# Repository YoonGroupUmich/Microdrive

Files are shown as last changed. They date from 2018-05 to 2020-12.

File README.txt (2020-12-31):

Microdrive designs for silicon probes.

Assembly instructions can be found in the assembly_instructions_rat1-2inch_v20.pdf file or at these links:
1. Microdrive assembly:  https://youtu.be/rjxaH515N64 
2. Probe attachment to microdrive:  https://youtu.be/2L5RHcbsU7o 
3. Probe recovery:   https://youtu.be/T5gyuZVKXo8 

The .stl files are optimized for Formlabs Form2 printer and Grey-v4/Clear-v4 Resin. For other printers and/or resins, some modifications may be necessary.

1 version is made available here:
v21: shell base 3.2 x 7.5 mm (WxL); height: 16 mm; travel distance 4.8 mm

This microdrive was modified based on Hiroyuki Miyawaki's design. The latest version of his microdrive is available at https://github.com/Mizuseki-Lab/microdrive.

The original idea of the drive is described in the following paper.

Micro-drive and headgear for chronic implant and recovery of optoelectronic probes Jinho Chung, Farnaz Sharif, Dajung Jung, Soyoun Kim & Sebastien Royer Scientific Reportsvolume 7, Article number: 2773 (2017) doi:10.1038/s41598-017-03340-5 https://www.nature.com/articles/s41598-017-03340-5

The designs are desitributed under GNU GPLv3 license.

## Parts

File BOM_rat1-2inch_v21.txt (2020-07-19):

Rat drive (1/2")

Qty	Name			Vendor		Item number		Notes			Link

7	00-90 nut		McMaster	92736A112					https://www.mcmaster.com/92736a112
2	00-90 screw 1/2"	McMaster	92482A235					https://www.mcmaster.com/92482a235
4	00-90 screw 1/4"	McMaster	93701A005					https://www.mcmaster.com/93701a005
1	rectangular header	DigiKey		SAM1067-40-ND					https://www.digikey.com/products/en?keywords=SAM1067-40-ND

1	T2 screwdriver		McMaster	52995A31		Only T2 is necessary!	https://www.mcmaster.com/52995a31
1	00-90 tap		McMaster	2504A14						https://www.mcmaster.com/2504a14
1	1.2 mm drill bit	McMaster	2958A29			Use to remove excess 	https://www.mcmaster.com/2958a29
									resin for 00-90 screws
									(if necessary).

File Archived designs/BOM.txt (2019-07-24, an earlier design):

Mouse drive

Qty	Name
3	00-90 nut (McMaster: 92736A112)
2	00-90 screw 3/8" (McMaster: 92453A856)
1	rectangular header (DigiKey: SAM1067-40-ND)

Rat drive (1/2")

Qty	Name
3	00-90 nut (McMaster: 92736A112)
2	00-90 screw 1/2" (McMaster: 92482A235)
1	rectangular header (DigiKey: SAM1067-40-ND)

Rat drive (5/8")

Qty	Name
3	00-90 nut (McMaster: 92736A112)
2	00-90 screw 5/8" (eBay: 00-90 X 5/8 Slot Fillister Head Machine Screws SS)
1	rectangular header (DigiKey: SAM1067-40-ND)

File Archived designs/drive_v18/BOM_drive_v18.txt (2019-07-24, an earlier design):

Rat drive (1/2")					
			
Qty	Name			Vendor		Item number	Notes			Link
					
7	00-90 nut		McMaster	92736A112				https://www.mcmaster.com/92736a112
2	00-90 screw 1/2" 	McMaster	92482A235				https://www.mcmaster.com/92482a235
4	00-90 screw 1/4" 	McMaster	93701A005				https://www.mcmaster.com/93701a005
1	rectangular header	DigiKey		SAM1067-40-ND				https://www.digikey.com/products/en?keywords=SAM1067-40-ND

Additional tools				
1	T2 screwdriver		McMaster	52995A31	Only T2 is necessary!	https://www.mcmaster.com/52995a31
1	00-90 Premium Tap 	Amazon							https://www.amazon.com/
1	1.2 mm drill bit	McMaster	2958A29		Any 1.2mm drill bit. 	https://www.mcmaster.com/2958a29
								Use to remove excess 
								resin for 00-90 screws 
								(if necessary).

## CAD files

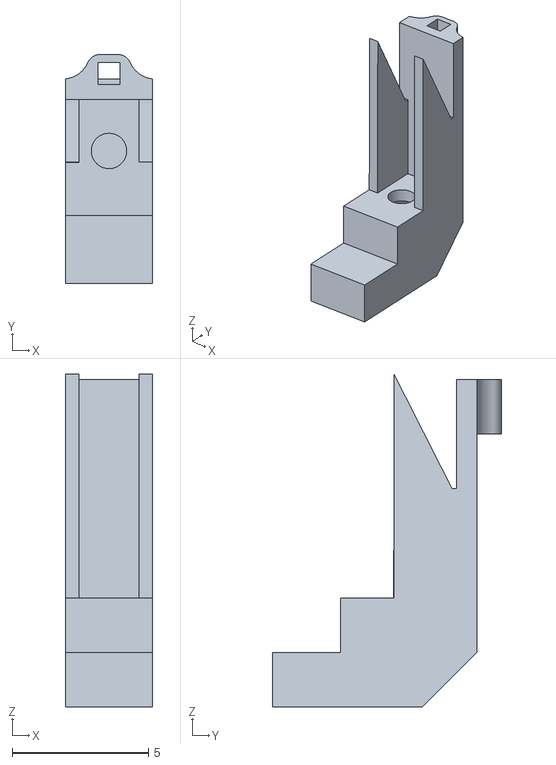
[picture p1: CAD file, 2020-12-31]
v21/shell_v21.stl
3.20 x 8.40 x 12.2

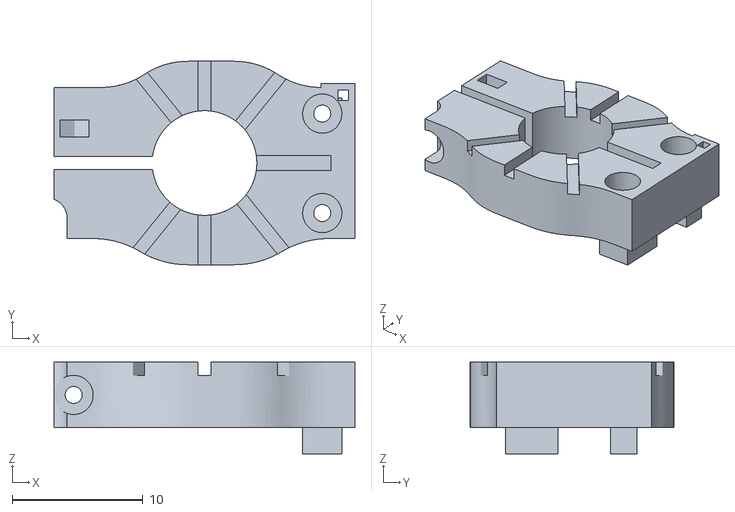
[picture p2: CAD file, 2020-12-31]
v21/stereotax_attachment_v21.stl
23.0 x 15.6 x 7.00

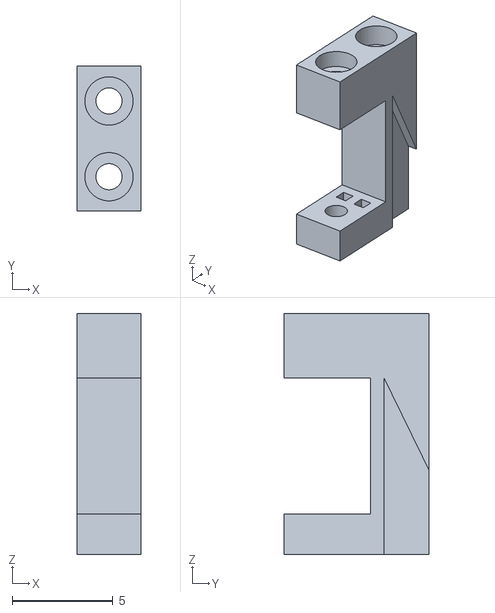
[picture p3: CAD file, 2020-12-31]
v21/drive_v21.stl
3.20 x 7.20 x 12.0

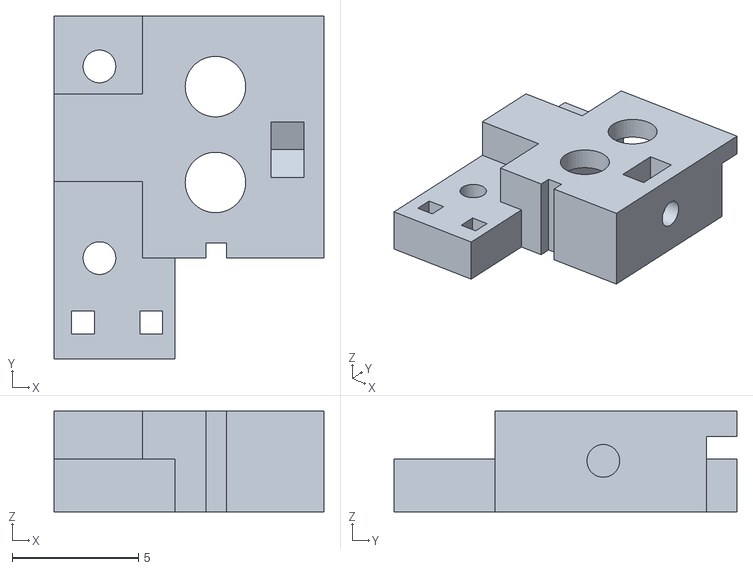
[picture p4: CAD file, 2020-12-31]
v21/drive_holder_v21.stl
10.7 x 13.6 x 4.00

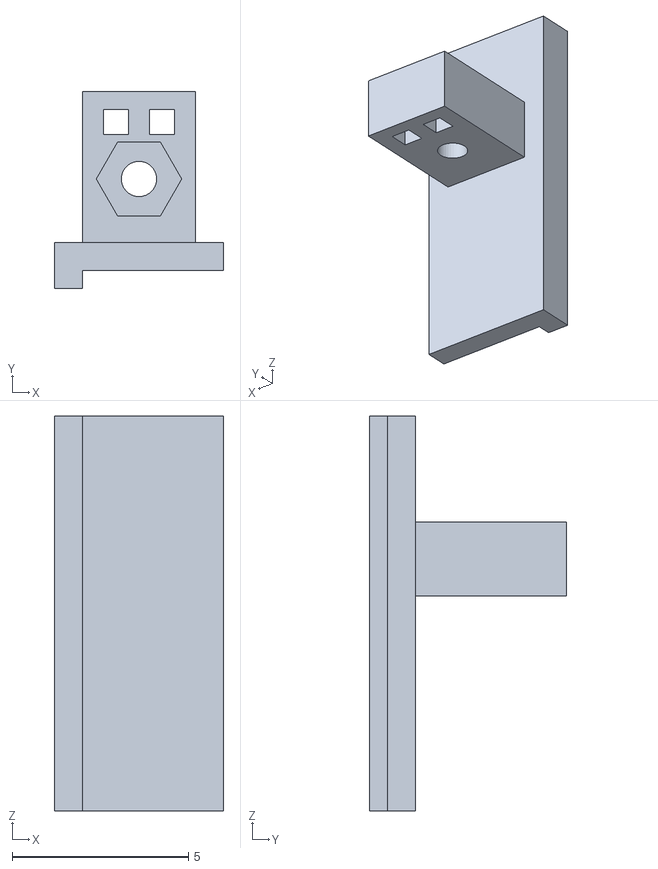
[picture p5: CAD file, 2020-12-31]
v21/arm_64ch_v3_v21.stl
4.80 x 5.58 x 11.2

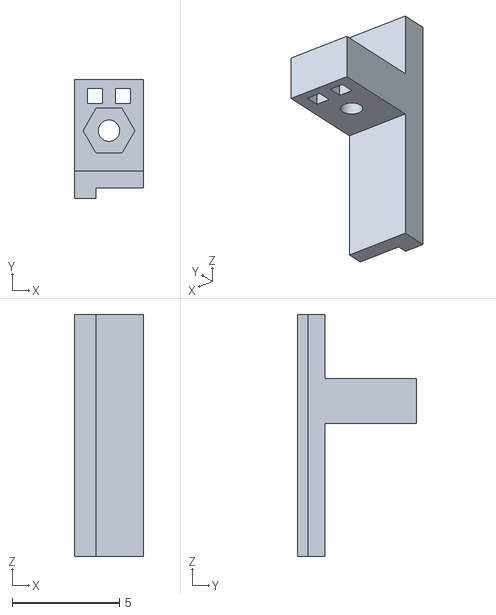
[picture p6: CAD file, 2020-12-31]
v21/arm_32ch_v21.stl
3.20 x 5.57 x 11.3

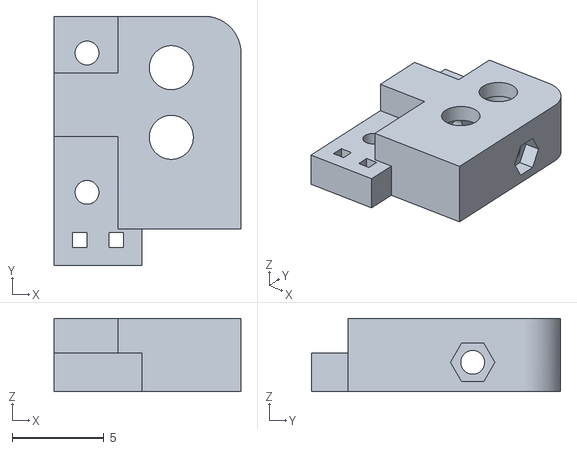
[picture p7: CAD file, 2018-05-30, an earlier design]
Archived designs/Mouse drive/attachement_misi_v6.stl
10.2 x 13.6 x 4.00

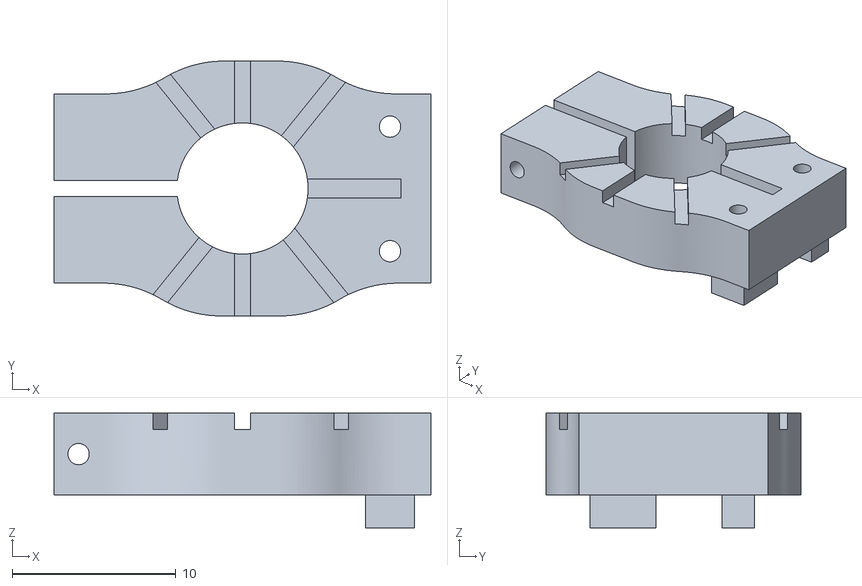
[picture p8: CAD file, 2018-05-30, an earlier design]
Archived designs/Rat drive/1-2-inch/holder_misi_v6.stl
23.0 x 15.6 x 7.00

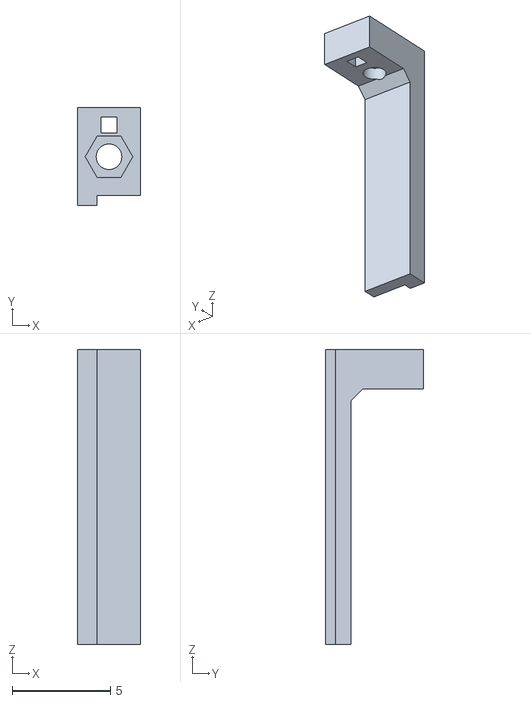
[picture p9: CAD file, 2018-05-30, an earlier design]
Archived designs/Rat drive/5-8-inch/arm_rat_5_8_inch_misi_v6.stl
3.20 x 4.97 x 15.0

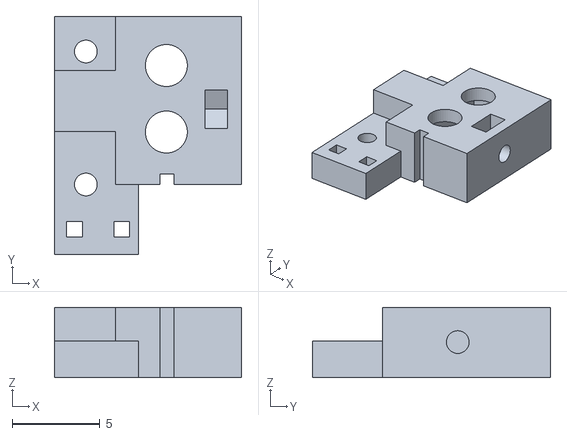
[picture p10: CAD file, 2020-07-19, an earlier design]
Archived designs/v20/drive_holder_v20.stl
10.7 x 13.6 x 4.00

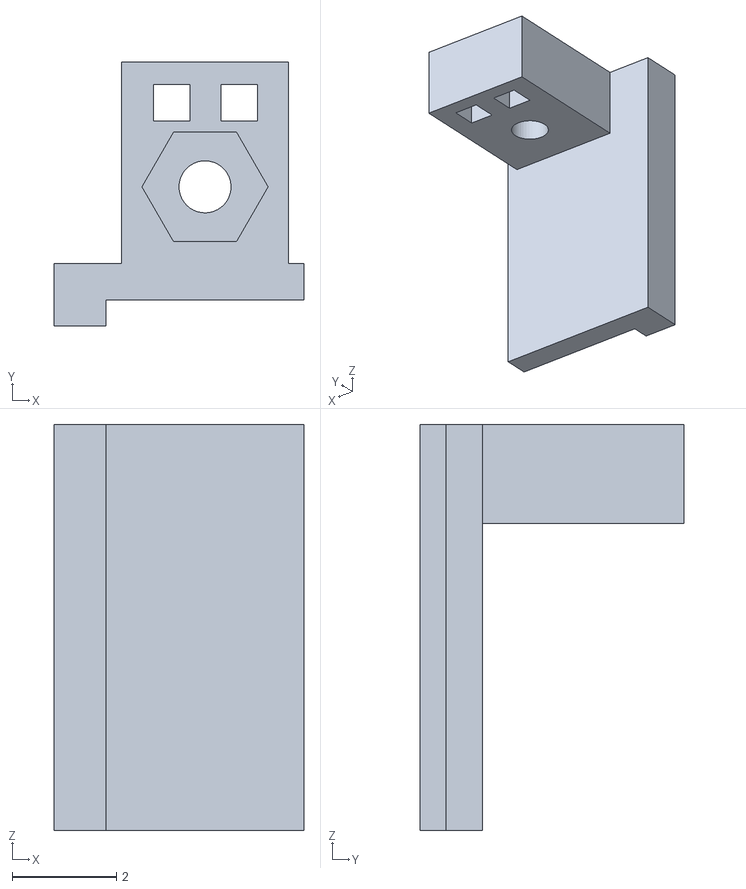
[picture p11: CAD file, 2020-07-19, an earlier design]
v20/arm_64ch_v2_v20.stl
4.80 x 5.08 x 7.80

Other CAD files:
Archived designs/drive_v18/shell.stl
Archived designs/drive_v18/stereotax attachment.stl
Archived designs/v20/drive_v20.stl
Archived designs/Mouse drive/arm_mouse_v6.stl
Archived designs/Mouse drive/drive_mouse_v6.stl
Archived designs/Mouse drive/shell_mouse_v6.stl
Archived designs/Rat drive/1-2-inch/arm_rat_1_2_inch_misi_v6.stl
Archived designs/Rat drive/1-2-inch/drive_rat_1_2_inch_misi_v6.stl
Archived designs/Rat drive/1-2-inch/shell_rat_1_2_inch_misi_v6.stl
Archived designs/Rat drive/5-8-inch/drive_rat_5_8_inch_misi_v6.stl
Archived designs/Rat drive/5-8-inch/shell_rat_5_8_inch_misi_v6.stl
Archived designs/drive_v18/arm_64ch.stl
Archived designs/drive_v18/drive holder.stl
Archived designs/drive_v18/drive.stl
Archived designs/v20/arm_32ch_v20.stl
Archived designs/v20/shell_v20.stl
Archived designs/v20/stereotax_attachment_v20.stl
v20/arm_32ch_v20.stl
v20/drive_v20.stl
v20/shell_v20.stl
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

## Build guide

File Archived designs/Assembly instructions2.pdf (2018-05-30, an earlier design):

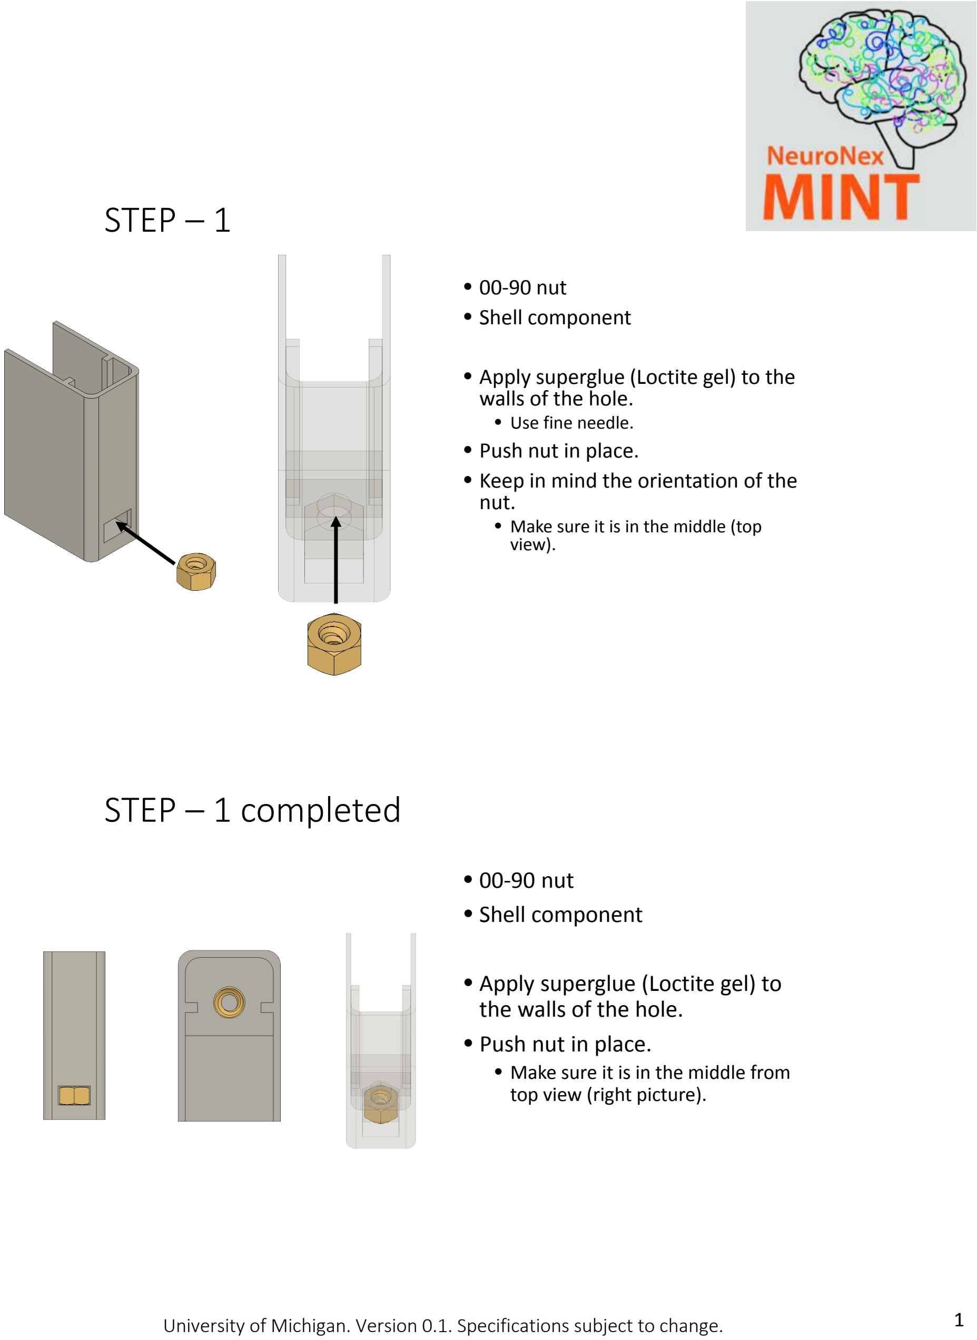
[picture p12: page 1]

### STEP –1

- 00‐90 nut
- Shell component
- Apply superglue (Loctite gel) to the walls of the hole.
- Use fine needle.
- Push nut in place.
- Keep in mind the orientation of the nut.
- Make sure it is in the middle (top view).

### STEP – 1 completed

- 00‐90 nut
- Shell component
- Apply superglue (Loctite gel) to the walls of the hole.
- Push nut in place.
- Make sure it is in the middle from top view (right picture).

University of Michigan. Version 0.1. Specifications subject to change.

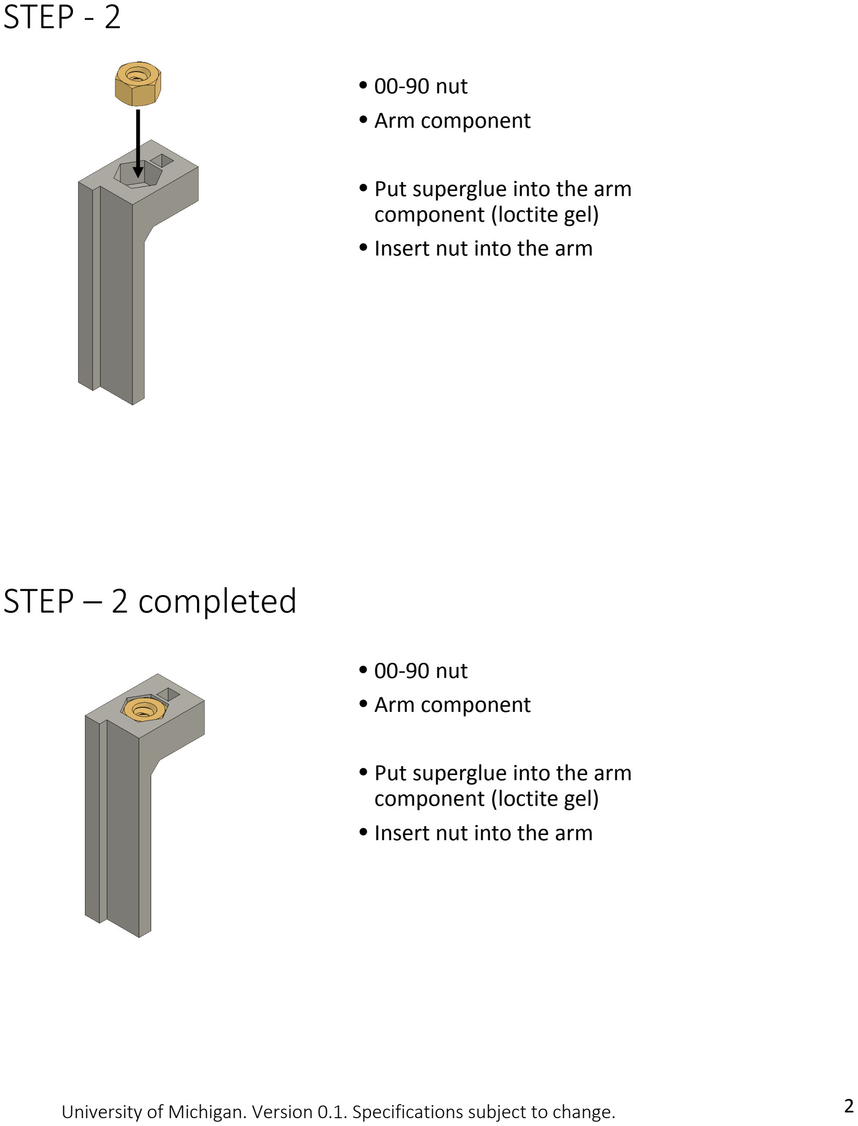
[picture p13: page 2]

### STEP ‐ 2

- 00‐90 nut
- Arm component
- Put superglue into the arm component (loctite gel)
- Insert nut into the arm

### STEP – 2 completed

- 00‐90 nut
- Arm component
- Put superglue into the arm component (loctite gel)
- Insert nut into the arm

### superglue

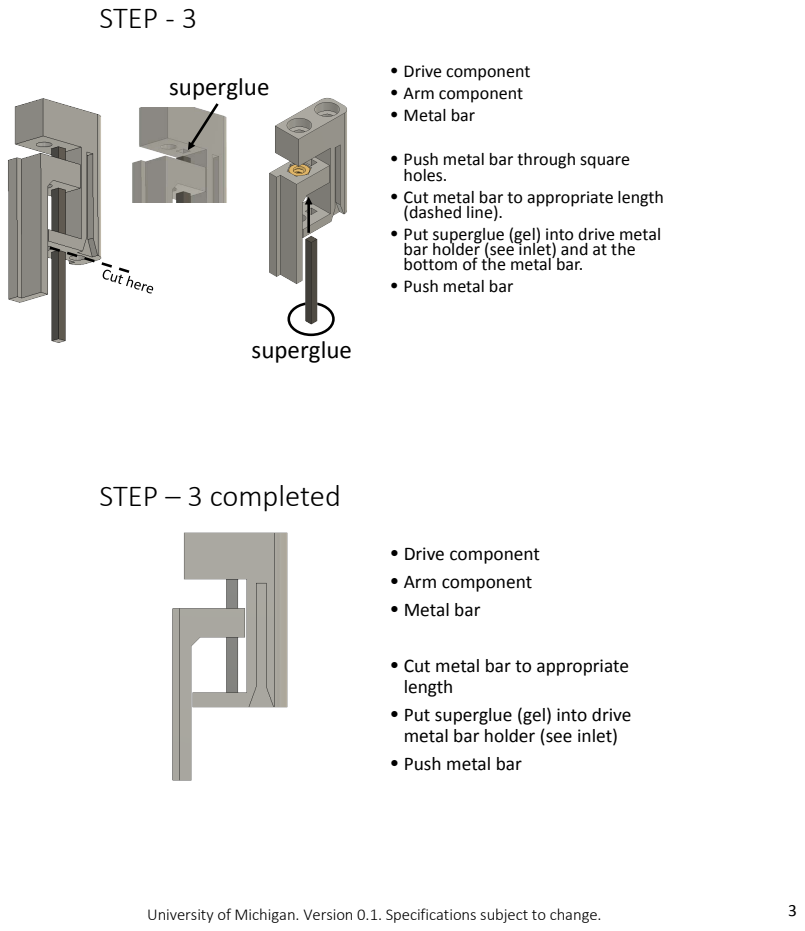
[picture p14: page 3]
STEP ‐ 3; • Drive component • Arm component • Metal bar; STEP – 3 completed; superglue

• Push metal bar through square holes.
• Cut metal bar to appropriate length (dashed line).
• Put superglue (gel) into drive metal
bar holder (see inlet) and at the
bottom of the metal bar.
• Push metal bar

• Cut metal bar to appropriate
length
• Put superglue (gel) into drive
metal bar holder (see inlet)

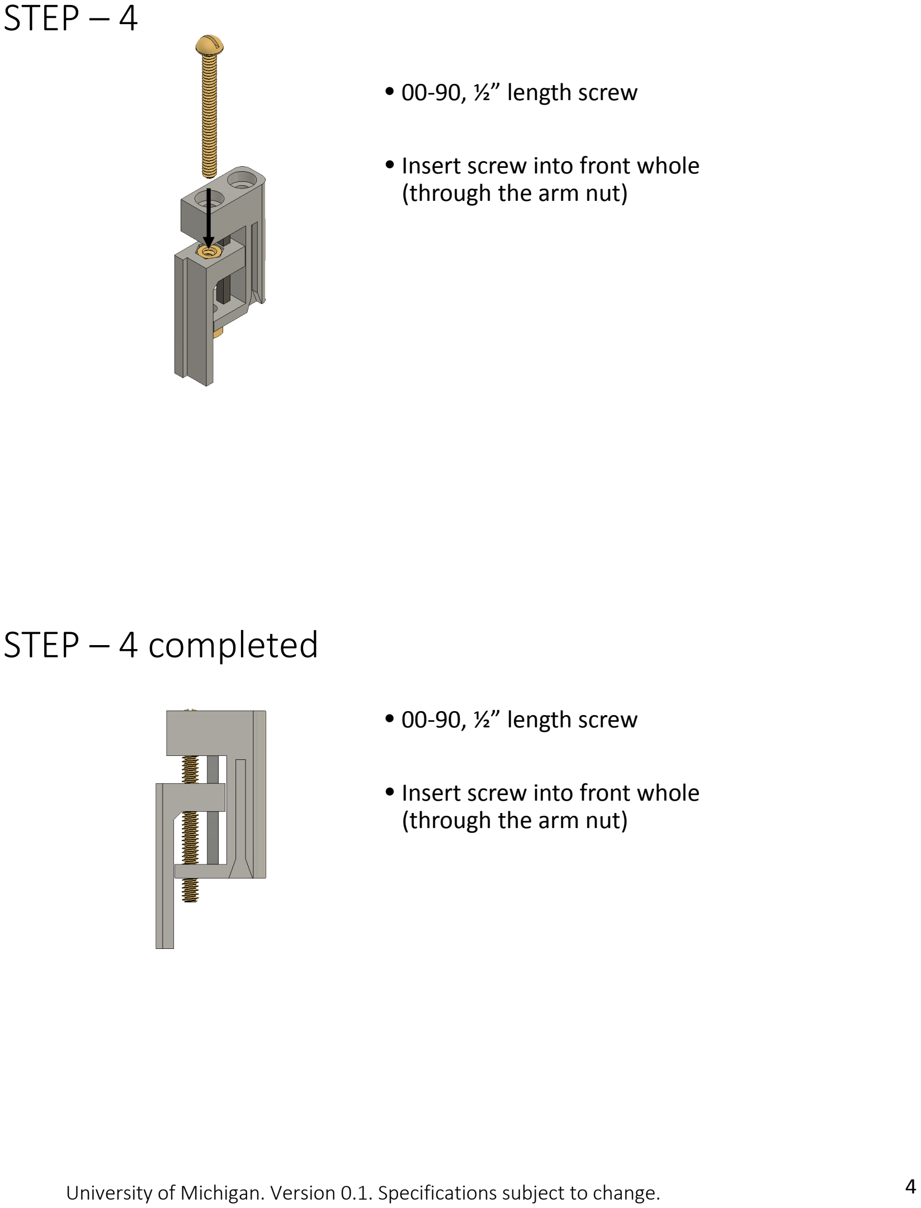
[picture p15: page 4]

### STEP –4

- 00‐90, ½” length screw
- Insert screw into front whole (through the arm nut)

### STEP –4 completed

- 00‐90, ½” length screw
- Insert screw into front whole (through the arm nut)

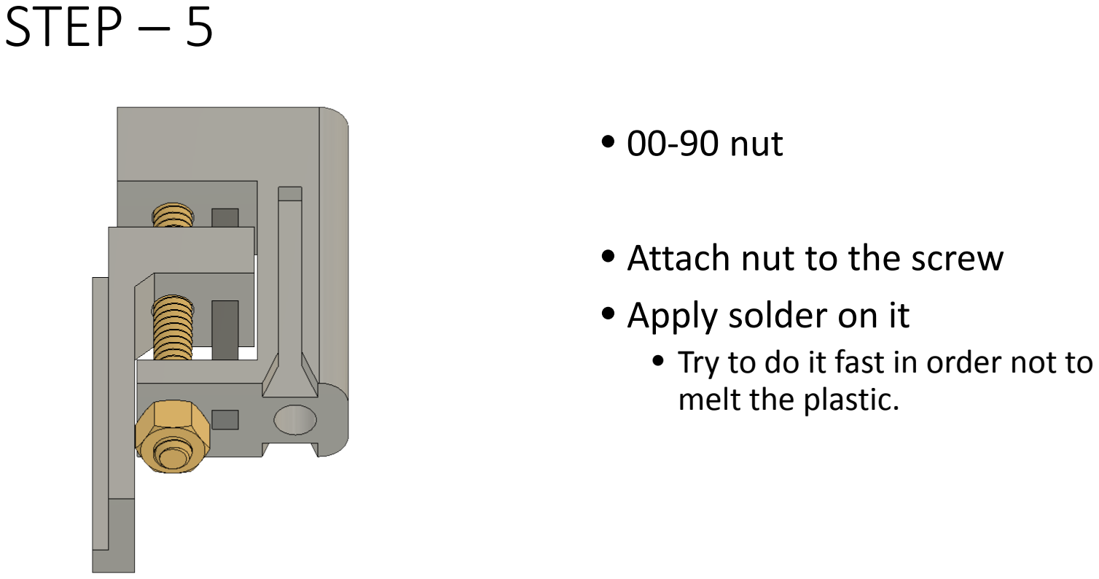
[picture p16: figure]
STEP –5; • 00‐90 nut; • Apply solder on it • Try to do it fast in order not to melt the plastic.

- Attach nut to the screw

### STEP –5 completed

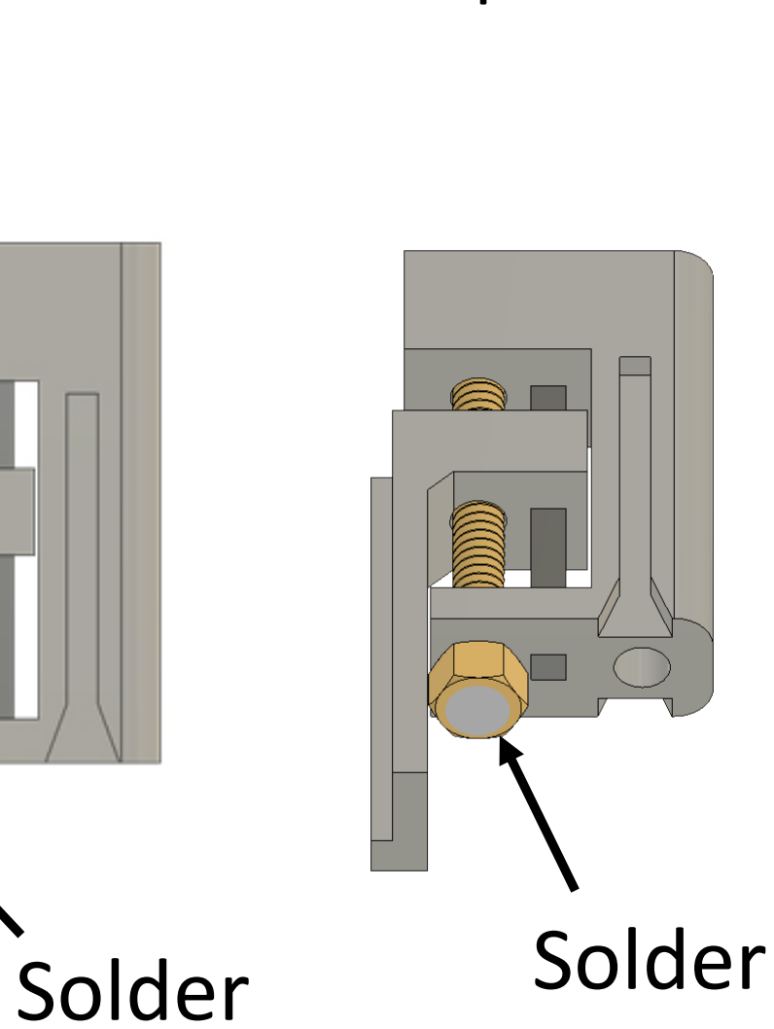
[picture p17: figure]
Solder Solder
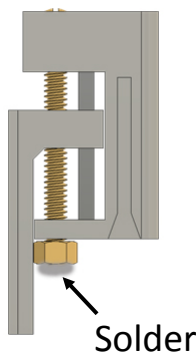
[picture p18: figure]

- 00‐90 nut
- Attach nut to the screw
- Apply solder on it
- Try to do it fast in order not to melt the plastic.

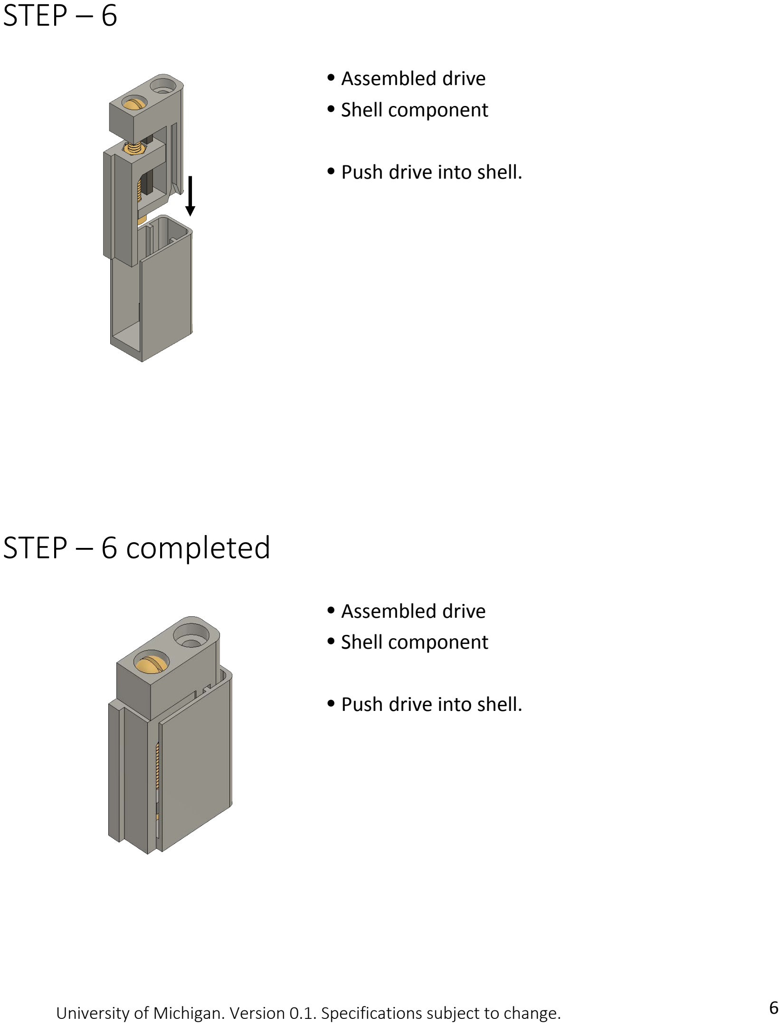
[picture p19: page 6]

### STEP –6

- Assembled drive
- Shell component
- Push drive into shell.

### STEP – 6 completed

- Assembled drive
- Shell component
- Push drive into shell.

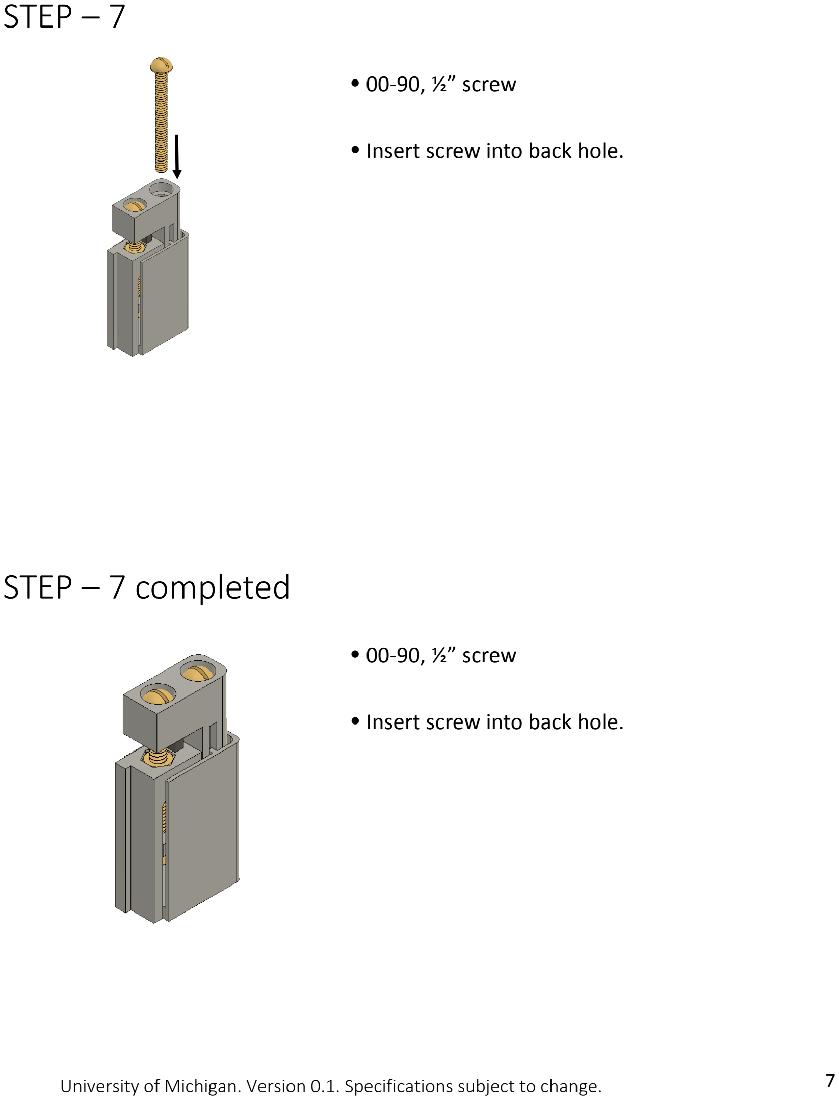
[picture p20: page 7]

### STEP –7

- 00‐90, ½” screw
- Insert screw into back hole.

### STEP – 7 completed

- 00‐90, ½” screw
- Insert screw into back hole.

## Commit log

2018-05-29 Added README file and drive.stl
    [drive_rat_1_2_inch_misi_v6.stl]
2018-05-30 Added Assembly instructions.
2018-05-30 Added BOM and Assembly instructions files.
2018-05-30 Added .stl files
    [arm_mouse_v6.stl, arm_rat_1_2_inch_misi_v6.stl, arm_rat_5_8_inch_misi_v6.stl, attachement_misi_v6.stl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]
2019-07-24 drive_v18 is uploaded
    [arm_64ch.stl, arm_mouse_v6.stl, arm_rat_1_2_inch_misi_v6.stl, arm_rat_5_8_inch_misi_v6.stl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]
2020-07-19 Uploaded v20
    [arm_32ch_v20.stl, arm_64ch.stl, arm_64ch_v2_v20.stl, drive holder.stl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]
